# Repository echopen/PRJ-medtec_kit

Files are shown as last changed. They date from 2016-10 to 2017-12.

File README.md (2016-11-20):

# Project


## Name
[`PRJ-medtec_kit`]()

## Title @lang=fr
Projet de kit d'expérimentation

## Title @lang=en
Experiment kit project

## About @lang=en
Designing a modular hardware development kit to spread the project and raise contributions.

## Challenge
[`CHG-medtec`]()

## Uses
This repository provid all is needed to make an echOpen kit. It is divided in six folders:  
+ **configurations**, in this folder one find the different working configuration to have a functional kit. It lists the différent daughter board to plug on a mother and the mecanic modules used.  
+ **electronic**, in this folder one can find the daughter boards sources, plans... And to software for the microcontrolers or FPGA.  
+ **installation**, in this folder one can find the instruction to download and install the software need by your computer (linux or windows user). There is also the instructions for installing boards such as arduino or RedPitaya and how to launch the kit.  
+ **license**, in this folder one can find the echOpen license.  
+ **mecanic**, in this folder one can find the sources for mecanic pieces.  
+ **miscellanous** contain informations about functions and interfaces.

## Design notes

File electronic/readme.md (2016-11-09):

# Informations

This folder contains the informations and sources to build the electrical parts (daughter boards) of our kit. It is composed of the folders:  
- **daughter_boards**, daughter board informations  
- **miscellianous**, kicad librairy files and datasheets of the electronic parts  
- **modules**, modules informations  

# Uses

If you want to access the informations and the sources a given daughter board juste go in the daughter_board folder (./daughter_board/DVC-) you are interesting in. Open the readme file with a markdown display tool (such as retext) where their is the needed information, the source are accessible simply by clicking on the link.

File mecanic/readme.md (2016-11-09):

# Informations

This folder contains the informations and sources to build the mecanical device for our kit. It is composed of two folders: **device** and **modules**. 

# Uses

If you want to access the informations and the sources a given device juste go in the device folder (./device/DVC-) you are interesting in. Open the readme file with a markdown display tool (such as retext) where their is the needed information, the source are accessible simply by clicking on the link.

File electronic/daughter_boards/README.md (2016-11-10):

In this repository one can find the different daughter boards of our systeme. Each daughter board can have different version.

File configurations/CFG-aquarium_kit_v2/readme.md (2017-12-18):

# Configuration
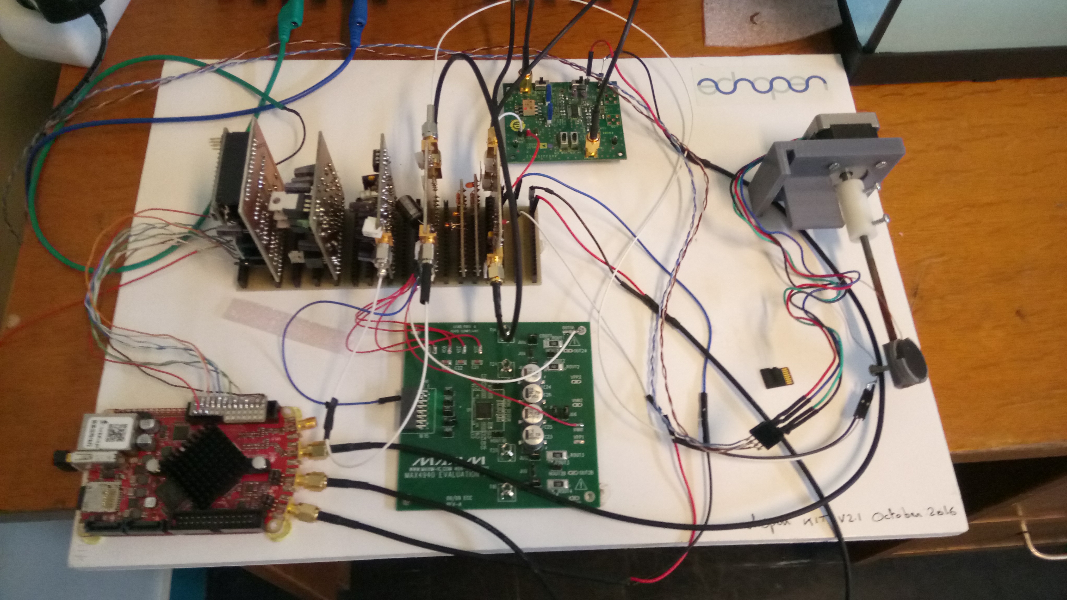
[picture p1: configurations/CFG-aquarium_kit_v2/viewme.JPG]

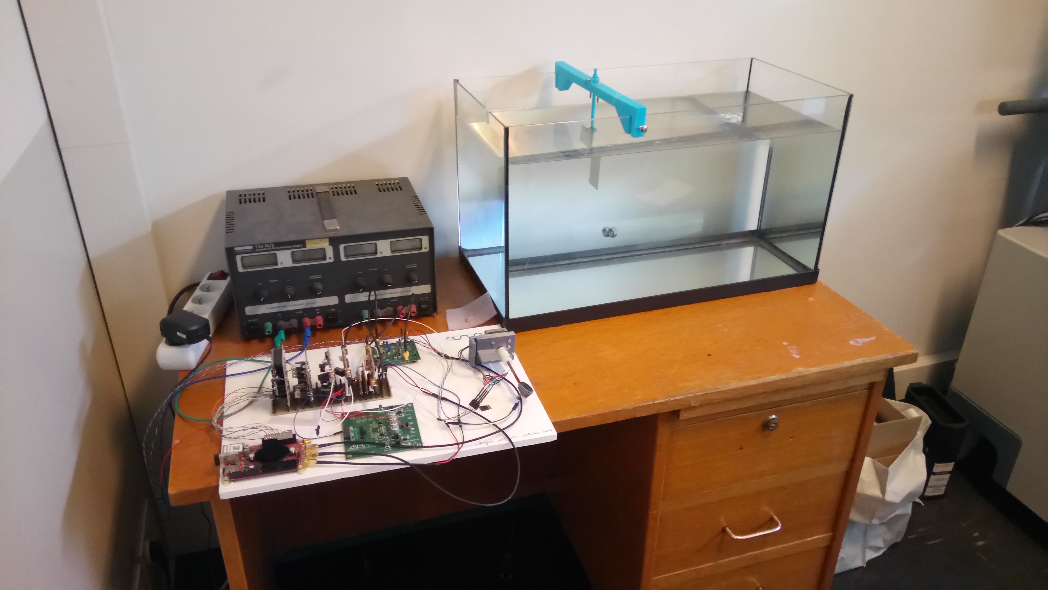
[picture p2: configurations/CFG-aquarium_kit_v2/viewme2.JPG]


## Name
[`CFG-aquarium_kit`]()

## Title
Kit 3.1 - Sept 2017

## About

## Uses
* [`DVC-aquarium`](../../mecanic/device/DVC-aquarium)
* [`MDL-transducer_v4`](../../electronic/modules/hardware/MDL-transducer/MDL-transducer_v4)
* [`MDL-power_supply_v1`](../../electronic/modules/hardware/MDL-power_supply/MDL-power_supply_v1)
* [`MDL-mother_board_v1`](../../electronic/modules/hardware/MDL-mother_board)
* [`MDL-redpitaya`](../../electronic/modules/hardware/MDL-redpitaya)
* [`MDL-motor_v2`](../../electronic/modules/hardware/MDL-motor/MDL-motor_v2)
* [`DB-supply_v1`](../../electronic/daughter_boards/DB-supply/DB-supply_v1)
* [`DB-high_voltage_v1`](../../electronic/daughter_boards/DB-high_voltage/DB-high_voltage_v1)
* [`DB-motor_control_v3`](../../electronic/daughter_boards/DB-motor_control/DB-motor_control_v3)
* [`DB-pulser_v3`](../../electronic/daughter_boards/DB-pulser/DB-pulser_v3)
* [`DB-filter_v1`](../../electronic/daughter_boards/DB-filter/DB-filter_v1)
* [`DB-envelope_detector_v1`](../../electronic/daughter_boards/DB-envelope_detector/DB-envelope_detector_v1)
* [`DB-tr_switch_tgc_v2`](../../electronic/daughter_boards/DB-tr_switch_tgc/DB-tr_switch_tgc_v2)

The sources of the code can be found [here](../../electronic/modules/software), select your configuration. Details on how to put the code on the arduino and the RedPitaya can be found [here](../../installation/linux_user/readme.md).

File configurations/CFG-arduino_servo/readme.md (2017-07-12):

# Configuration
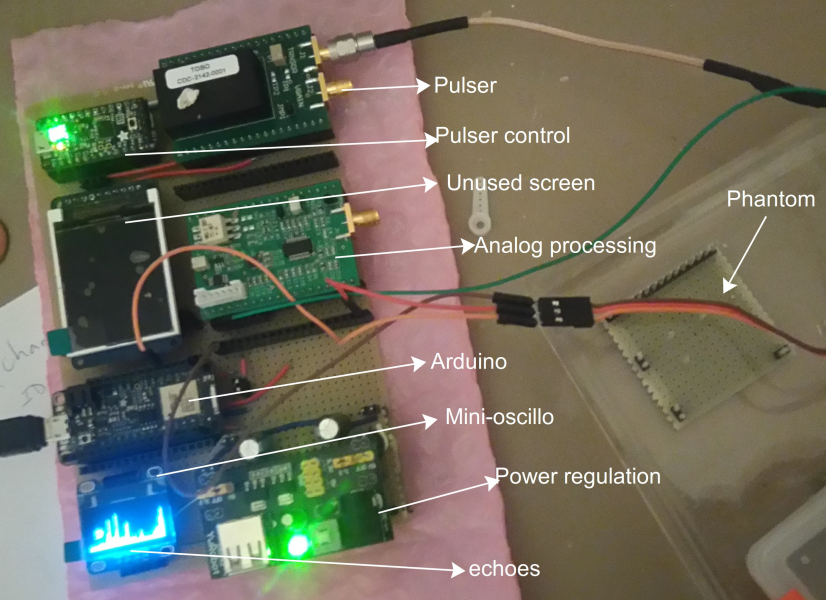
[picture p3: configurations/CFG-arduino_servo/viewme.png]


## Name
[`CFG-arduino_servo`]()

## Title
Dev kit v.1.1

## About

## Uses

* [`MDL-pulser_control`](../../electronic/modules/hardware/MDL-pulser_control)
* [`MDL-piezoservo`](../../electronic/modules/hardware/MDL-power_supply/MDL-piezoservo)
* [`MDL-breadboard_supply`](../../electronic/modules/hardware/MDL-breadboard_supply)
* [`MDL-analog_processing_ic`](../../electronic/modules/hardware/MDL-analog_processing_ic)
* [`MDL-pulser_ic`](../../electronic/modules/hardware/MDL-pulser_ic)
* [`MDL-arduino_wifi_daq`](../../electronic/modules/hardware/MDL-arduino_wifi_daq)

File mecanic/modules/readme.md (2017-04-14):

To make the kit, one will have to print (with a 3d printer):
- MDL-motor_support wich is the part where we will fix the motor, this part afer will be put on an aquarium border. Need to precise the screw to put on (x4)
- MDL-rod_fixation wich is a piece to link a metal rod (MDL-rod) with the motor. There is two holes to put 2 screw the upper one (motor size) need to stick out so it will hit the motor_support when initialising (searching it's 0). The second one use to fix the rod. (diameter of the screw)
MDL-transducer depend on your transducer better to make your own. When we will have (ENS) typical transducer we will make an appropritate support.

MDL-phantom_support depend on the size of you aquarium (this one is for xxx mm large).
MDL-stick must be place in MDL-phantom
MDL-plate_support was made to put a thin plate for tests. It plug with MDL-stick
The three last MDL are not necessary

For 3dprinting use MDL-x.stl files. If you want to make modifications one can use freecad (open the .igs file) modify and then export in .stl file (mesh formats files).

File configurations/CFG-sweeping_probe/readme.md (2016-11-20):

# Configuration
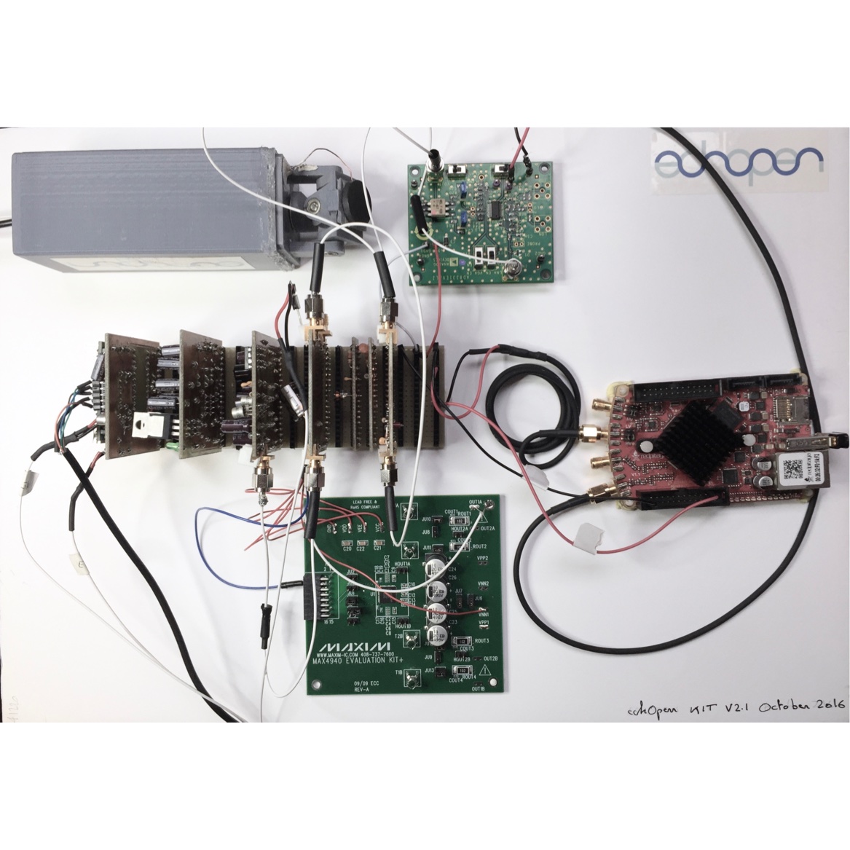
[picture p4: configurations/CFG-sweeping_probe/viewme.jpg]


## Name
[`CFG-sweeping_probe`]()

## Title
Kit 2.1 - Oct 2016

## About

## Uses
* [`DVC-sweeping_probe`](../../mecanic/device/DVC-sweeping_probe)
* [`MDL-transducer_v4`](../../electronic/modules/hardware/MDL-transducer/MDL-transducer_v4)
* [`MDL-power_supply_v1`](../../electronic/modules/hardware/MDL-power_supply/MDL-power_supply_v1)
* [`MDL-mother_board_v1`](../../electronic/modules/hardware/MDL-mother_board)
* [`MDL-redpitaya`](../../electronic/modules/hardware/MDL-redpitaya)
* [`DB-supply_v1`](../../electronic/daughter_boards/DB-supply/DB-supply_v1)
* [`DB-high_voltage_v1`](../../electronic/daughter_boards/DB-high_voltage/DB-high_voltage_v1)
* [`DB-motor_control_v1`](../../electronic/daughter_boards/DB-motor_control/DB-motor_control_v1)
* [`DB-pulser_v2`](../../electronic/daughter_boards/DB-pulser/DB-pulser_v2)
* [`DB-filter_v1`](../../electronic/daughter_boards/DB-filter/DB-filter_v1)
* [`DB-envelope_detector_v1`](../../electronic/daughter_boards/DB-envelope_detector/DB-envelope_detector_v1)
* [`DB-tr_switch_tgc_v1`](../../electronic/daughter_boards/DB-tr_switch_tgc/DB-tr_switch_tgc_v1)

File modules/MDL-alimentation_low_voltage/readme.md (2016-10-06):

# Module
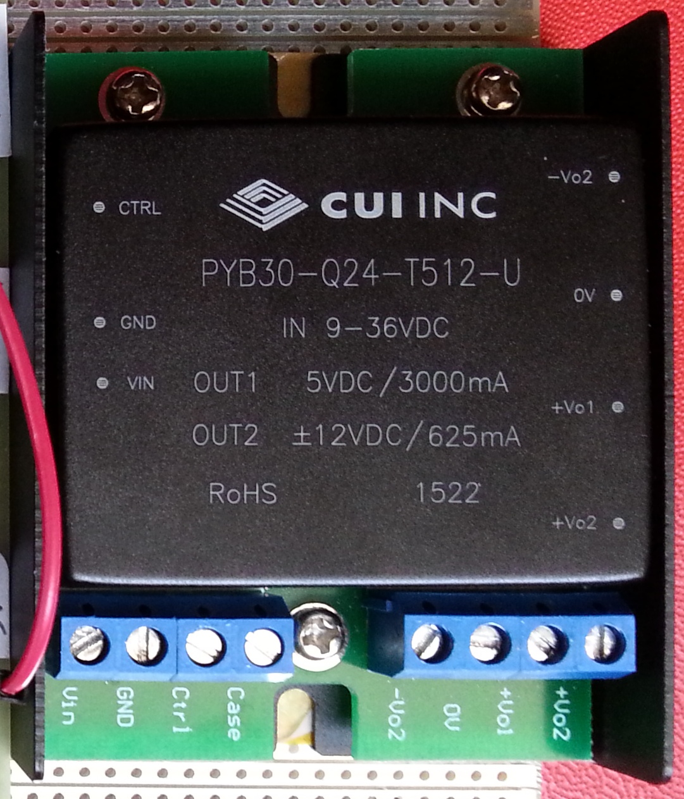
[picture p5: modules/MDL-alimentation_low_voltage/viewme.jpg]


## Name
[`MDL-alimentation_low_voltage`]()

## Title
Low voltage (+5v, +3.3v, ...) alimentation

## Description

## Uses
* external +5v

## Produce
* [`ITF-10_gnd`](../../interfaces/ITF-10_gnd)
* [`ITF-29_5v`](../../interfaces/ITF-29_5v)

## Functions
* TODO, ex : [`FCT-sensing`](../../functions/FCT-sensing)

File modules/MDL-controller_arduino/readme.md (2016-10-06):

# Module
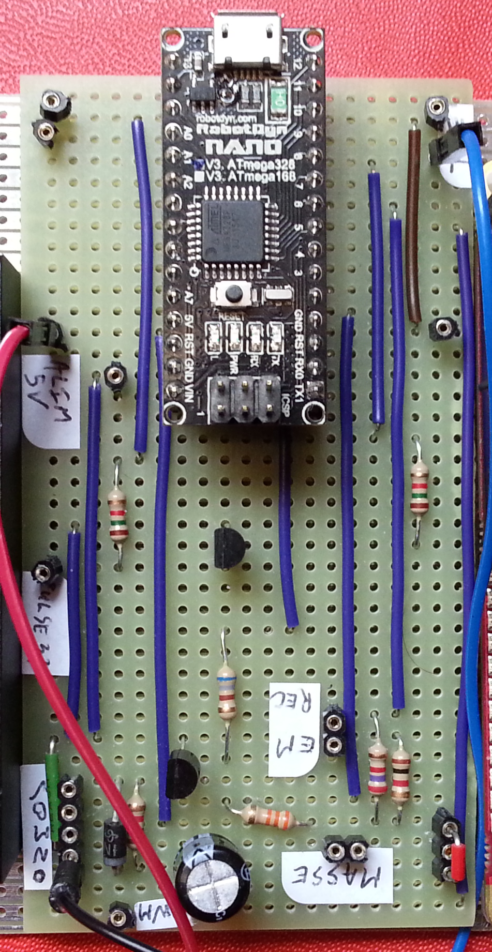
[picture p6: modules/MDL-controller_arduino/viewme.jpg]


## Name
[`MDL-controller_arduino`]()

## Title
Arduino µC with E/S for driving CC motor

## Description

## Uses
[`ITF-10_gnd`](../../interfaces/ITF-10_gnd)

## Functions
TODO, ex : [`FCT-sensing`](../../functions/FCT-sensing)

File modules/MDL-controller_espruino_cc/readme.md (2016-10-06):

# Module
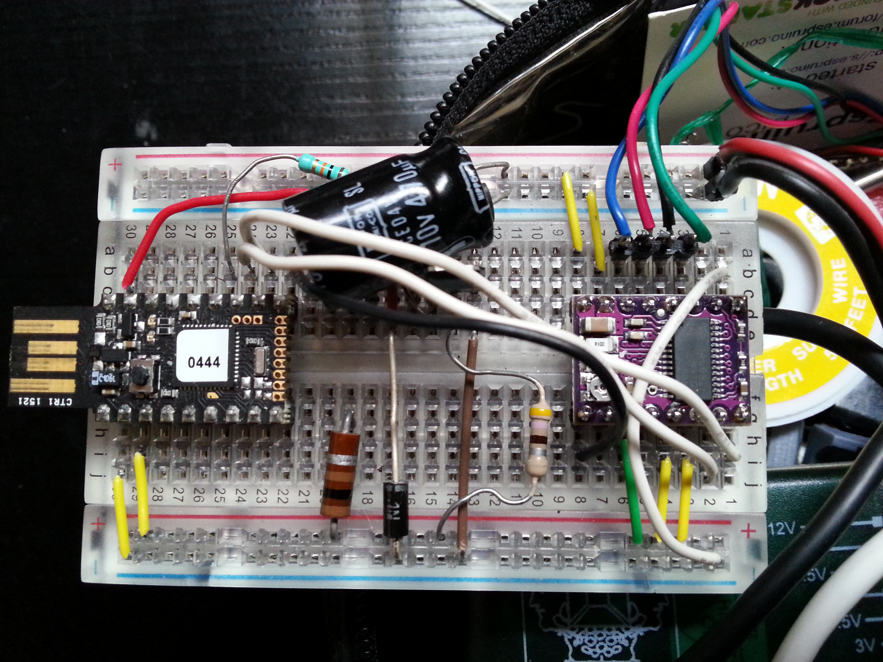
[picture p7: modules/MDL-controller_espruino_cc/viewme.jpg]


## Name
[`MDL-controller_espruino_cc`]()

## Title
Espruino µC with E/S for driving CC motor

## Description

## Uses
[`ITF-10_gnd`](../../interfaces/ITF-10_gnd)

## Functions
TODO, ex : [`FCT-sensing`](../../functions/FCT-sensing)

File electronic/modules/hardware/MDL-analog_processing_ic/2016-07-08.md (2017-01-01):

# First hands-on with Goblin : an overview [](@description First experiment on 08th July 2016)

## What does it do?

This [Goblin](/electronic/modules/hardware/MDL-analog_processing_ic/) board aims at getting a signal, and giving access to key points within the signal processing chain for ultrasound imaging, namely:

* Getting access to a TGC
* Getting the enveloppe of the signal
* Cleaning the signal before feeding in the on-board SPI ADC

All key signals are accessible, and jumpers, as well as pots, enable on-board fine-tuning of the signals. [See more details on the __testing session__, to see the behavior of the board on a oscillo](/electronic/modules/hardware/MDL-analog_processing_ic/2016-07-08.md).

## View

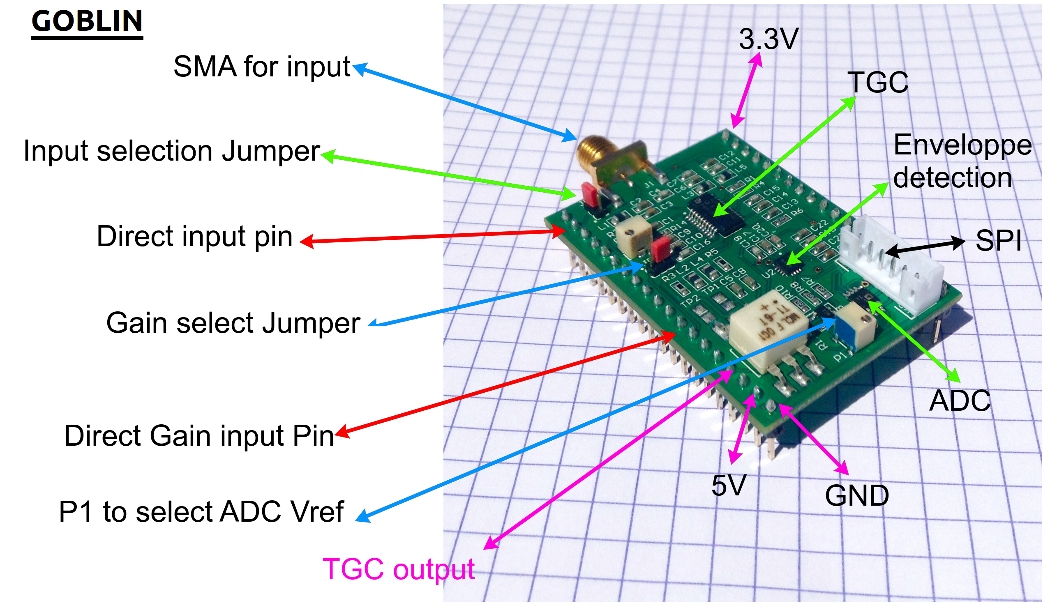
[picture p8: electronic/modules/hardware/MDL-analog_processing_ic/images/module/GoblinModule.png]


## Detailed view

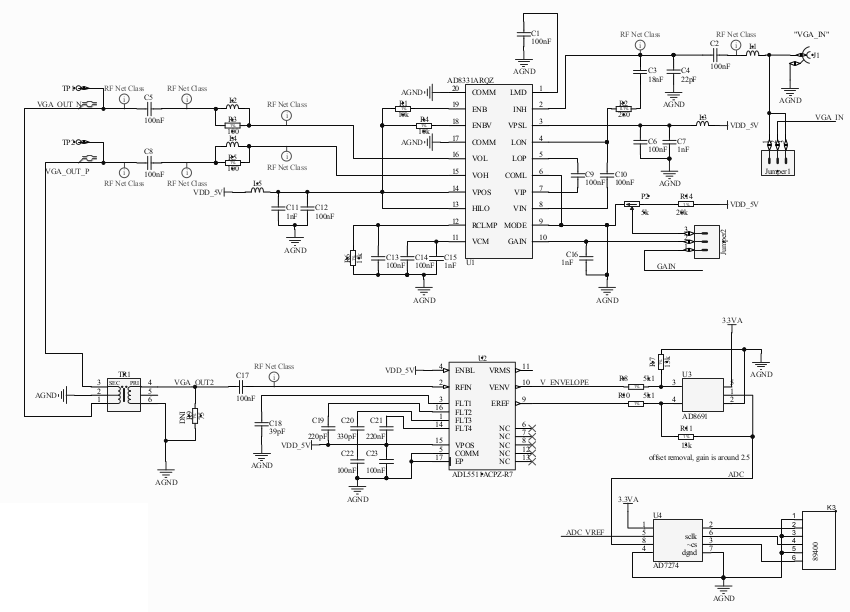
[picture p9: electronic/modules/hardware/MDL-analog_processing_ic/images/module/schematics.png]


## Principles

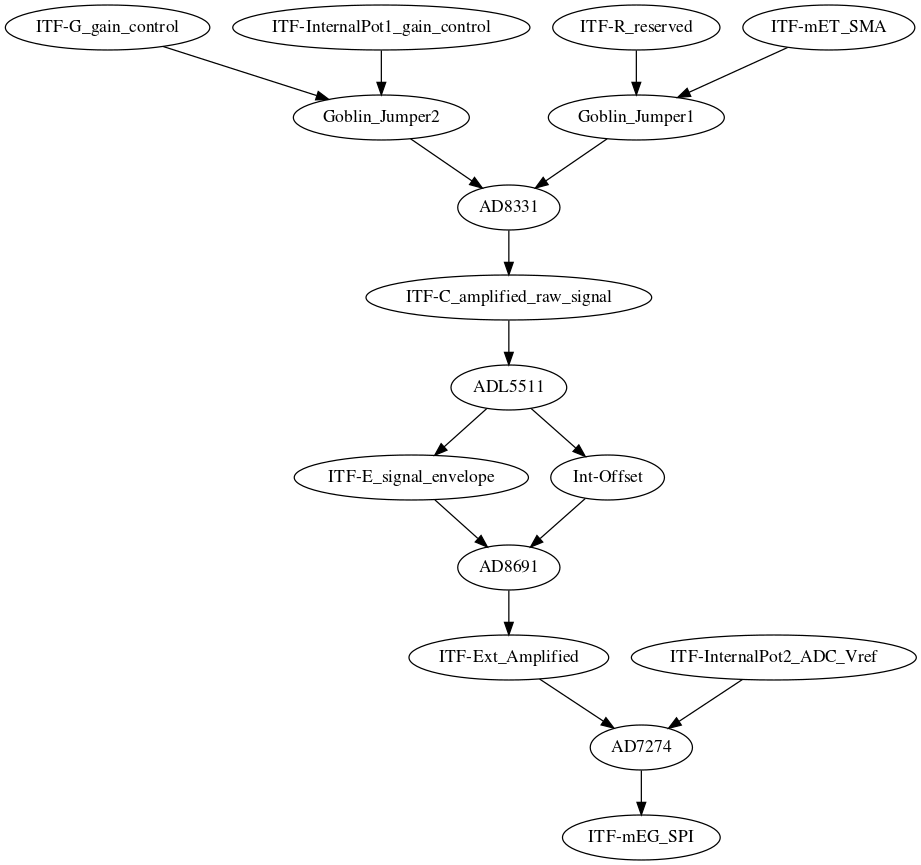
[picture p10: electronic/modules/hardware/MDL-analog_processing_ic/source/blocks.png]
Block schema


## Testing the board

### Signal in vs Signal out of the TGC

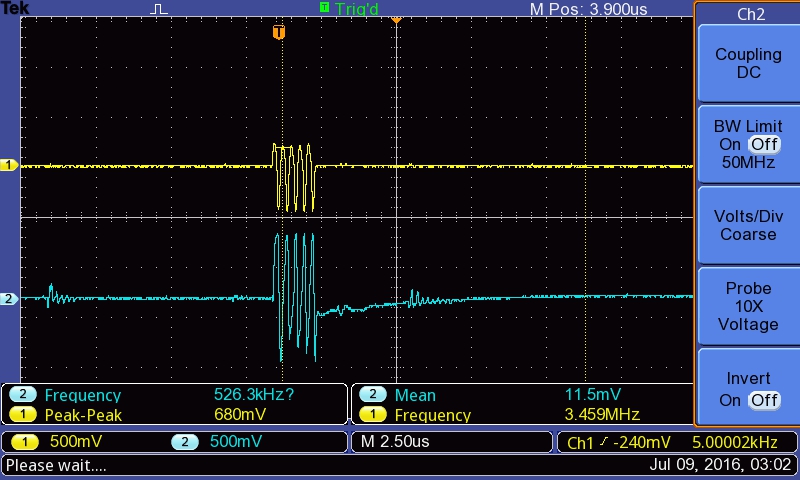
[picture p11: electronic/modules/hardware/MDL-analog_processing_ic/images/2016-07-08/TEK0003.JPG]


### Trying with different frequencies

#### At 3 MHz

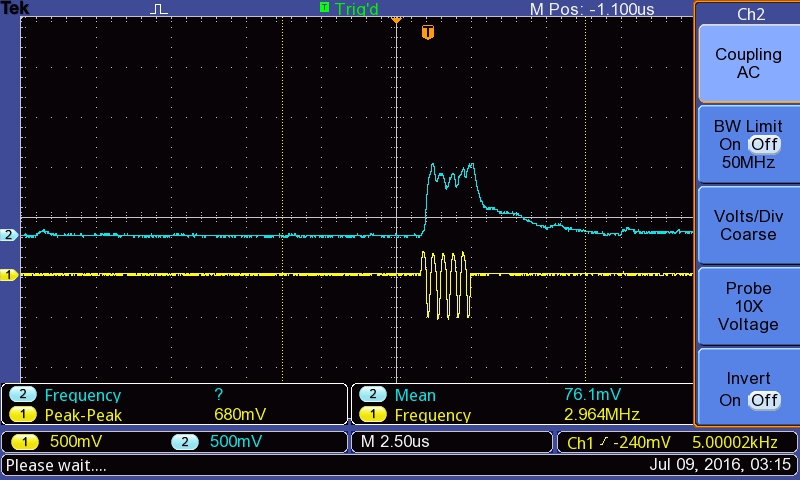
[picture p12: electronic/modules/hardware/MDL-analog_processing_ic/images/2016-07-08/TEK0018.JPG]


#### At 5MHz

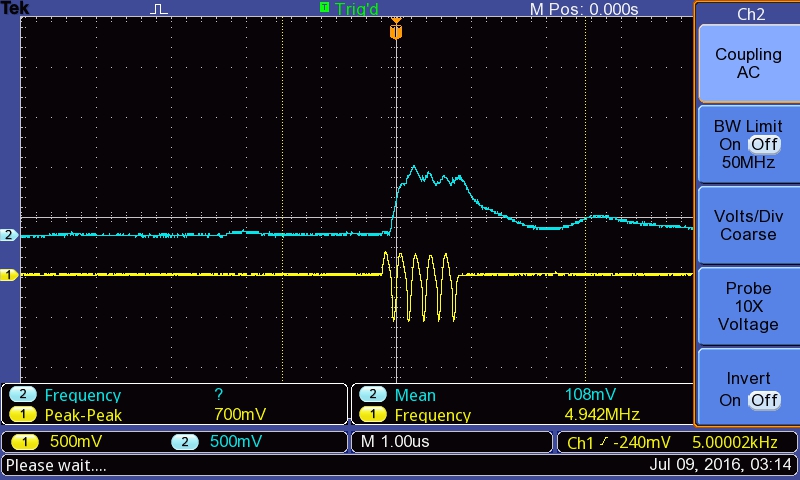
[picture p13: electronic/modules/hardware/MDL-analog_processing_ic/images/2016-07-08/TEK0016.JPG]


#### At 7.5MHz

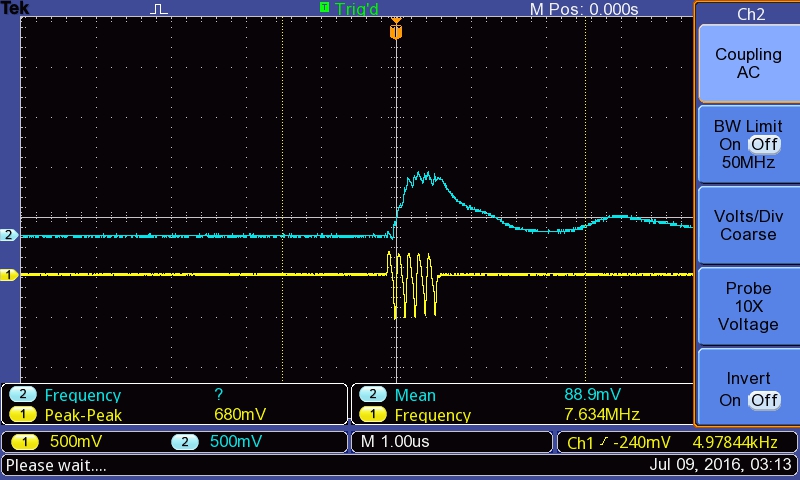
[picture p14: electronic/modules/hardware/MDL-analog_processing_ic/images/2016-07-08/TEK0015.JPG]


#### At 10MHz

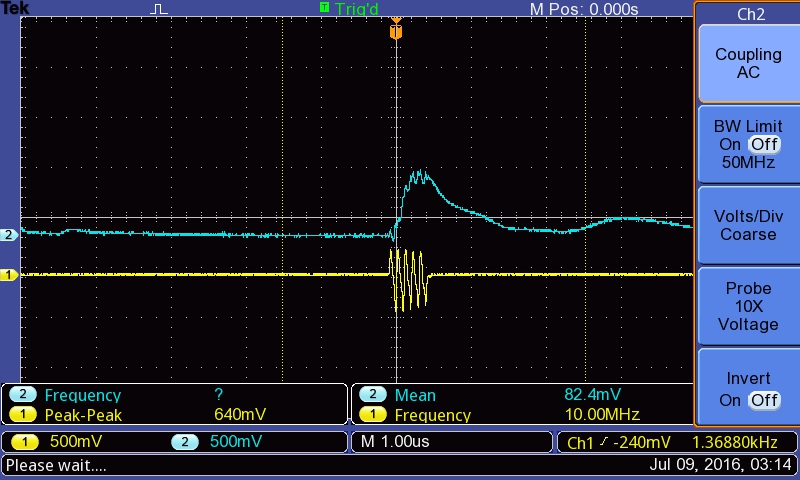
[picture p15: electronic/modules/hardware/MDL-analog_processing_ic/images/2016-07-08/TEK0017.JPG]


### Difference between enveloppe and ADC input?

-> the offset is removed, there's also a small gain (x2).

See below: there's an offset at the enveloppe detection (~RMS), which is removed. Enveloppe is 500mV before, comes at 1V+ afterwards.

#### Before the AOP

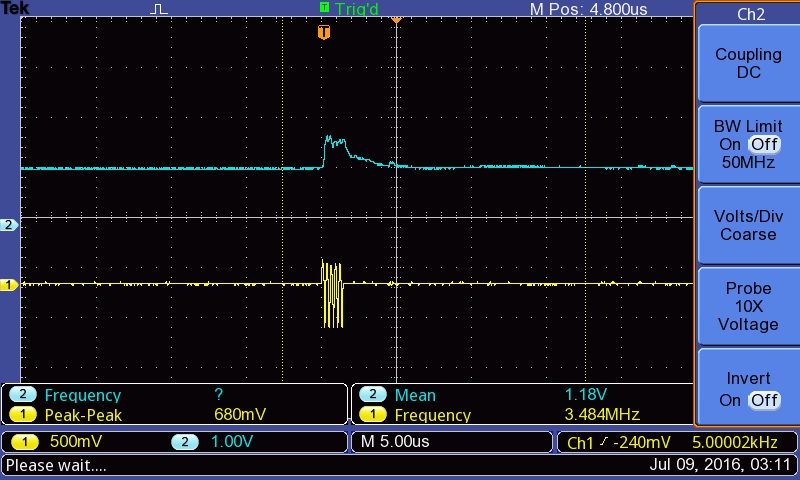
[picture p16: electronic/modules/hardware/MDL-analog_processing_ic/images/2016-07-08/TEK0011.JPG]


#### After the AOP

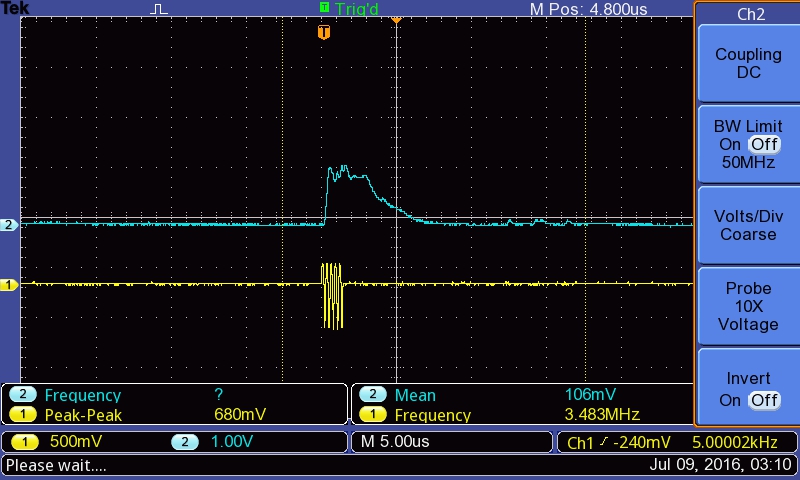
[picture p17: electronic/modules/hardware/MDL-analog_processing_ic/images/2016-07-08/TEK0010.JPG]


TODO: Table

## To know more

### Components that have been used

* TGC:
* Enveloppe detection:
* ADC:

TODO =)

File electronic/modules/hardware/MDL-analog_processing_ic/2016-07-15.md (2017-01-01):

# Second hands-on with Goblin : an overview [](@description Second work with Goblin)

## What does it do?

This [Goblin](/electronic/modules/hardware/MDL-analog_processing_ic/) board aims at getting a signal, and giving access to key points within the signal processing chain for ultrasound imaging, namely:

* Getting access to a TGC
* Getting the enveloppe of the signal
* Cleaning the signal before feeding in the on-board SPI ADC

All key signals are accessible, and jumpers, as well as pots, enable on-board fine-tuning of the signals. [See more details on the __testing session__, to see the behavior of the board on a oscillo](/electronic/modules/hardware/MDL-analog_processing_ic/2016-07-08.md). __Beware, this session had a poor energy supply quality, so the 5V got quite low. The [new log](/electronic/modules/hardware/MDL-analog_processing_ic/2016-07-15.md), covers it better.

## Testing the board using 0.2V in gain input (max can be 1V, that's ~20% gain used)

### Just after the TGC : A 60mV signal becomes a 300mV signal.

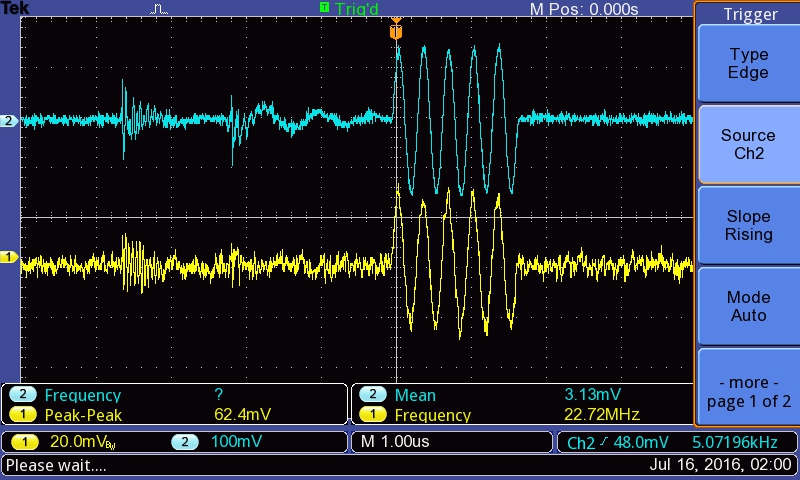
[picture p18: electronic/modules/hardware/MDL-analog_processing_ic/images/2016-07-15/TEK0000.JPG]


### Which becomes, after enveloppe detection, a 400mV enveloppe.

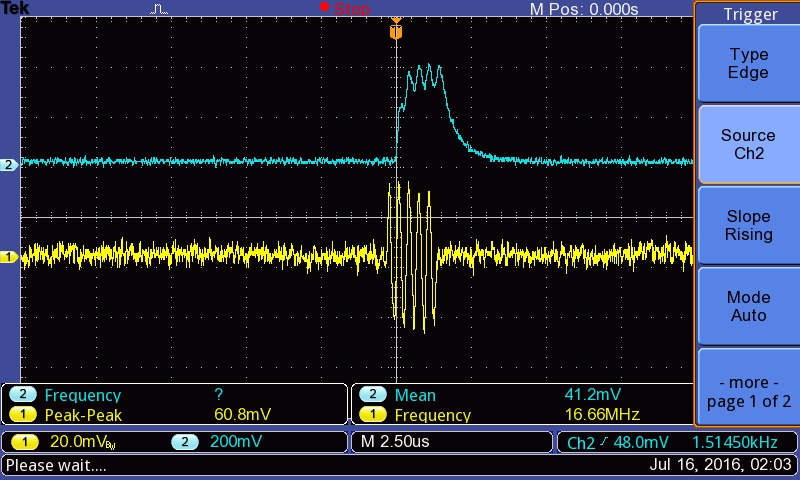
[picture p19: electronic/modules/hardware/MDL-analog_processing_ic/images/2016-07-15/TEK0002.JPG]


### Likewise, a 120mVpp signal becomes a 750mV enveloppe, clean.



## View



## Detailed view



## Principles

Block schema

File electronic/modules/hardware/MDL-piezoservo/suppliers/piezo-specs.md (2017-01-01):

# Interested in a monoelement transducer for an open science project

Dear XXX,

I'm currently working with an open-source echography association  (echopen.org) based in Paris, which is currently looking for transducers that could be used for medical imaging for the design of its tool. I have heard your name through former colleagues at the ESPCI Paristech, and would like to investigate if you could provide us with appropriate transducers for this project.
 
We are developing a mechanical, single-element-design probe, operating at three frequencies, so with three series of piezos, with the following details:

* One at 3.5 MHz, focal zone between 50 and 150 mm,
* One at 5 MHz , focal zone between 30 and 105 mm,
* One at 7.5 MHz , focal zone between 10 and 75 mm.

With respect to the dimensions, ideally, we are looking for a low-footprint transducer (less than 2 cm diameter) and minimal depth for the physical size of the transducer (we don't need casing, though we'd need the backing and soldering already done) to integrate in our prototype. We'll be finetuning additional parameters as soon as we make progress on the probe itself. we would need:

* Diameter: as small as possible, ideally below 15mm for the 3.5MHz, 8mm for the 5MHz and 5mm for the 7.5MHz - without casing.
* Thickness: as small as possible.

Would it be possible for you to provide us with a quote for a first, to test one, along with the corresponding specs? Also, even using rough figures, we'd be keen on having an idea of the budget that'd be required to produce a couple, from 2 or 3 to 50 at the prototyping stage.

Looking forward to reading from you,

Best regards,

Luc

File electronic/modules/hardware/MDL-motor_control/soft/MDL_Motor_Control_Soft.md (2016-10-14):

Module: MDL_Motor_Control_Hard

Function: sensing

Sub-Function: emitting

We use a single transducer, it must sweep an given angle in order to make 2D imaging, this can be done with a movement convertor. But if we want to uniformely scan the angle, we have to know exactly where and when the transducer is located. Depend on the solution, this can be ordered or calculated by the software.

Solutions: 

version: V1.0

date: 15/04/2016

technology: home made

contributor: Jérôme

Source:

[https://github.com/echopen/Prototype_software/blob/master/V1/Arduino/motor_pulse/motor_pulse.ino](https://github.com/echopen/Prototype_software/blob/master/V1/Arduino/motor_pulse/motor_pulse.ino)

An API will be made soon.

Flowchart:

The function Velocity is made on interruption, each time the encoder of the motor change from LOW to HIGH level, the velocity is calculated. Due to RedPitaya speed limitation (on measurement), with have limited the motor "virtual" velocity to Vlim. So even if the motor is too fast, the time between two pulse will be long enough to make an acquisition.

The function Interpolation determine the angle difference of the motor position between each pulse. With this angle and the instantaneous velocity we can determined the time between each pulse. The interpolation function give a constant dz on a line perpendicular to the probe.

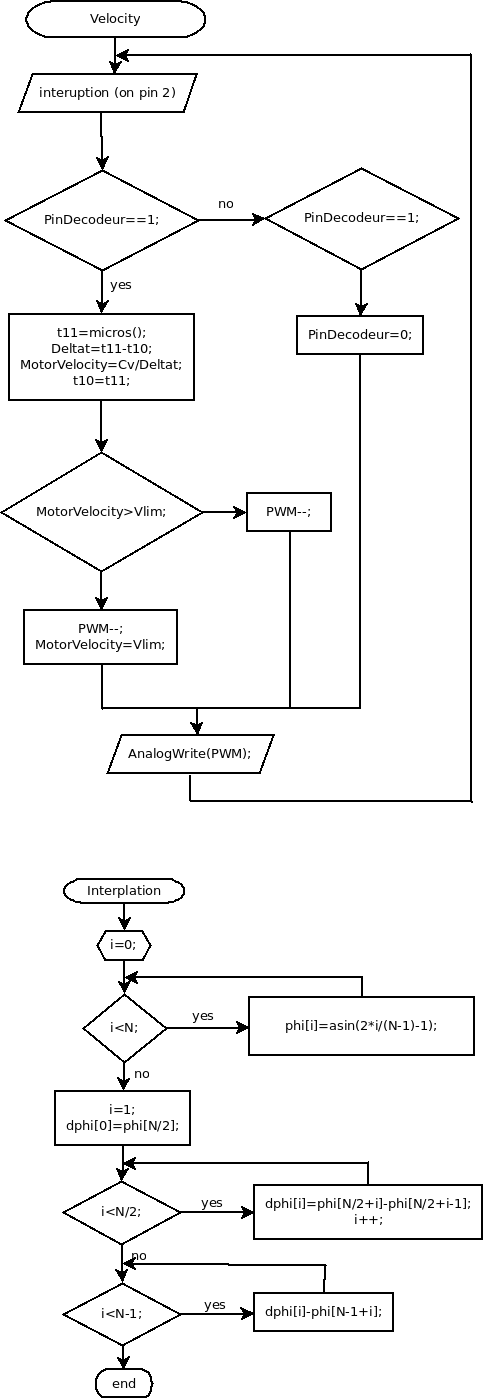
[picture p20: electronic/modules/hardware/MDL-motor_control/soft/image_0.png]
image alt text


version: V2.0

date: 07//2016

technology: IC

contributor: Feng

Source:

[https://github.com/echopen/Prototype_software/blob/master/Arduino_Nano/Stepper_Motor/stepper%20motor.ino](https://github.com/echopen/Prototype_software/blob/master/Arduino_Nano/Stepper_Motor/stepper%20motor.ino)

An API will be made soon.

Flowchart:

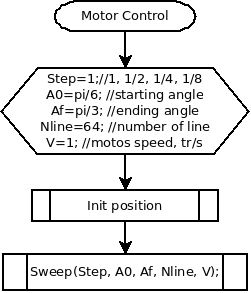
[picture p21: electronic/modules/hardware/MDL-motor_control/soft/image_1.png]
image alt text


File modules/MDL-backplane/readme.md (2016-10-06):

# Module
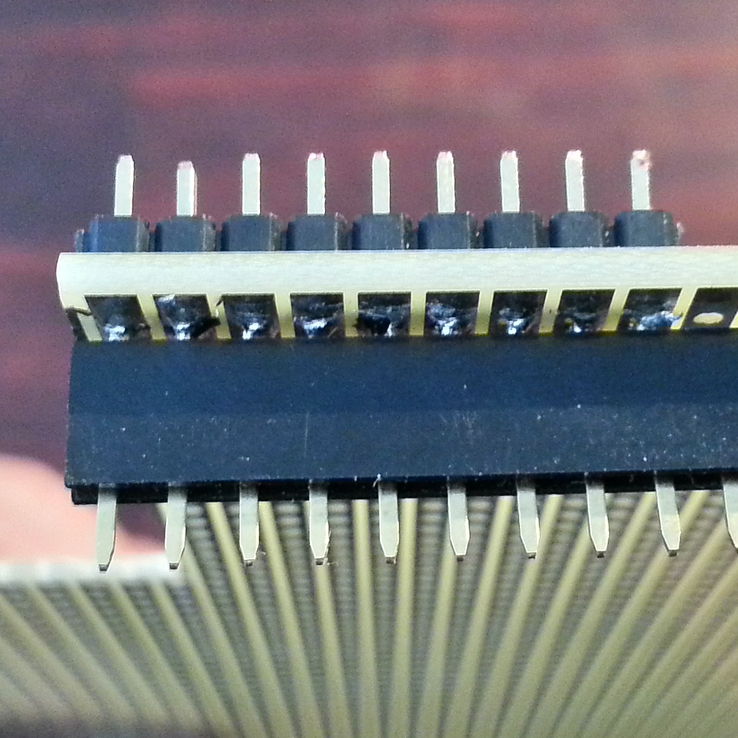
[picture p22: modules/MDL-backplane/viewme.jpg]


## Name
[`MDL-backplane`]()

## Title
Backplane card

## Description

## Uses
[`ITF-10_gnd`](../../interfaces/ITF-10_gnd)

## Functions
TODO, ex : [`FCT-sensing`](../../functions/FCT-sensing)

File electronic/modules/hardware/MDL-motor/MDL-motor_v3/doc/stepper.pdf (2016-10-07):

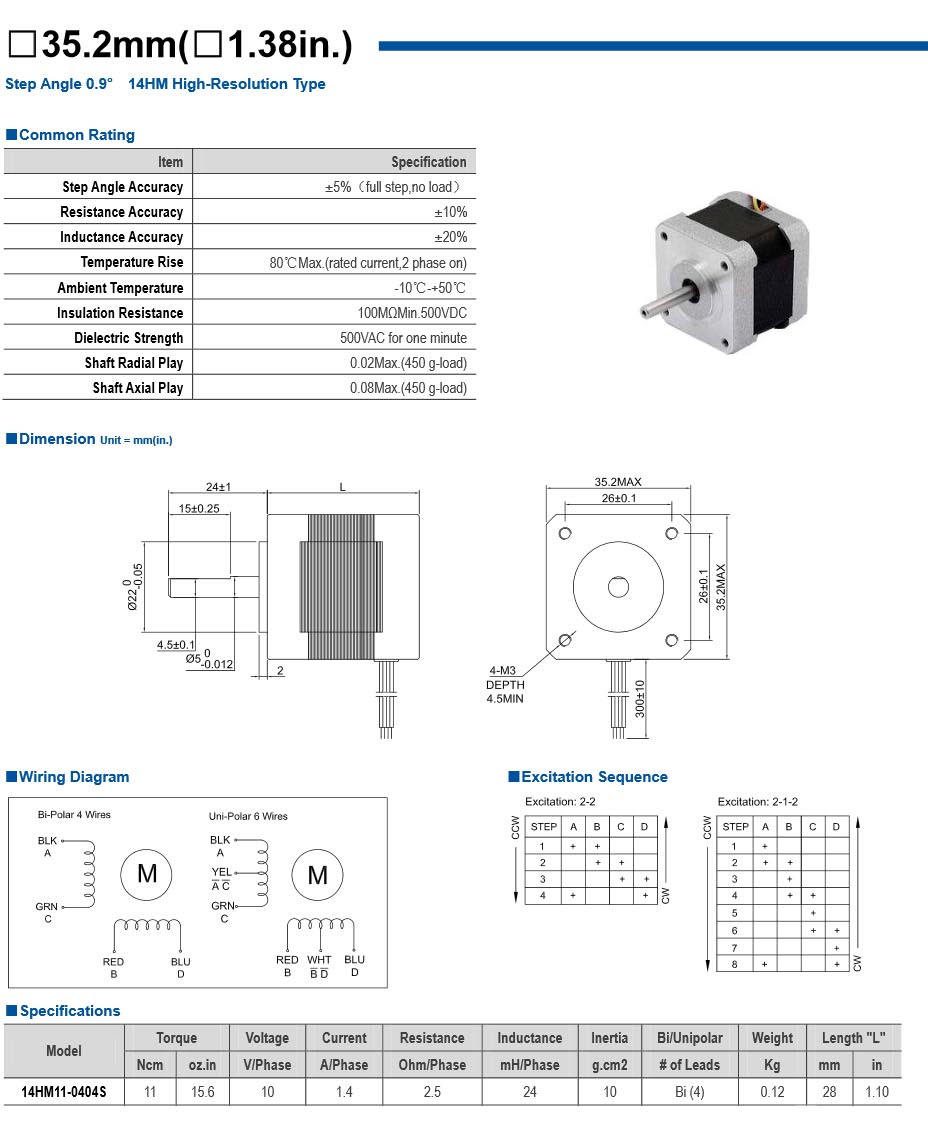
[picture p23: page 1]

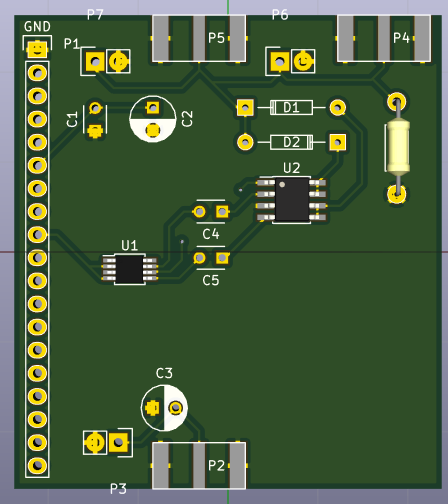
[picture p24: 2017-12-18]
electronic/daughter_boards/DB-pulser/DB-pulser_v3/images/pcb.png

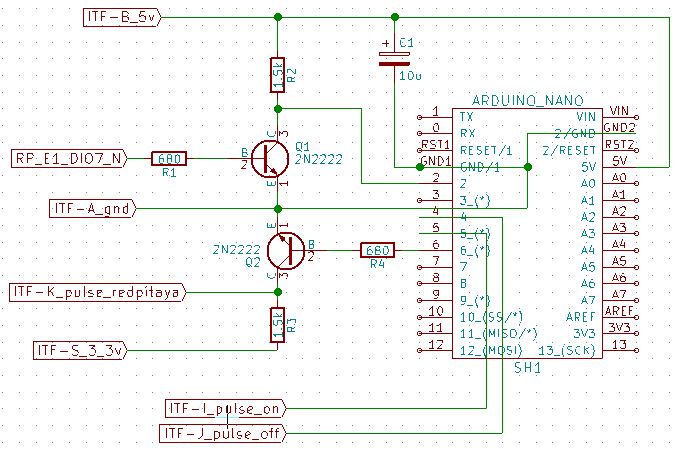
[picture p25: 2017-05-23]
electronic/modules/hardware/MDL-ucontroler/MDL-ucontroler_v2/images/scheme.png

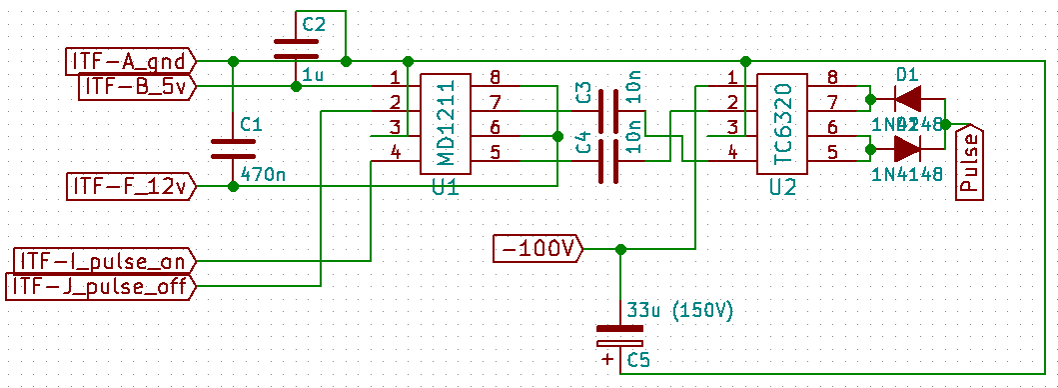
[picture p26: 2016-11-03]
electronic/modules/hardware/MDL-pulser/MDL-pulser_v3/images/scheme.png

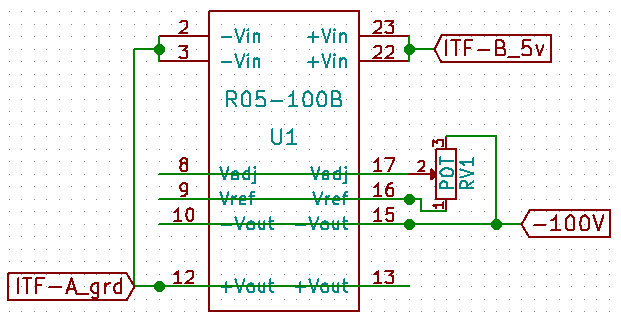
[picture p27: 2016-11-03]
electronic/modules/hardware/MDL-high_voltage/MDL-high_voltage_v2/images/scheme.png

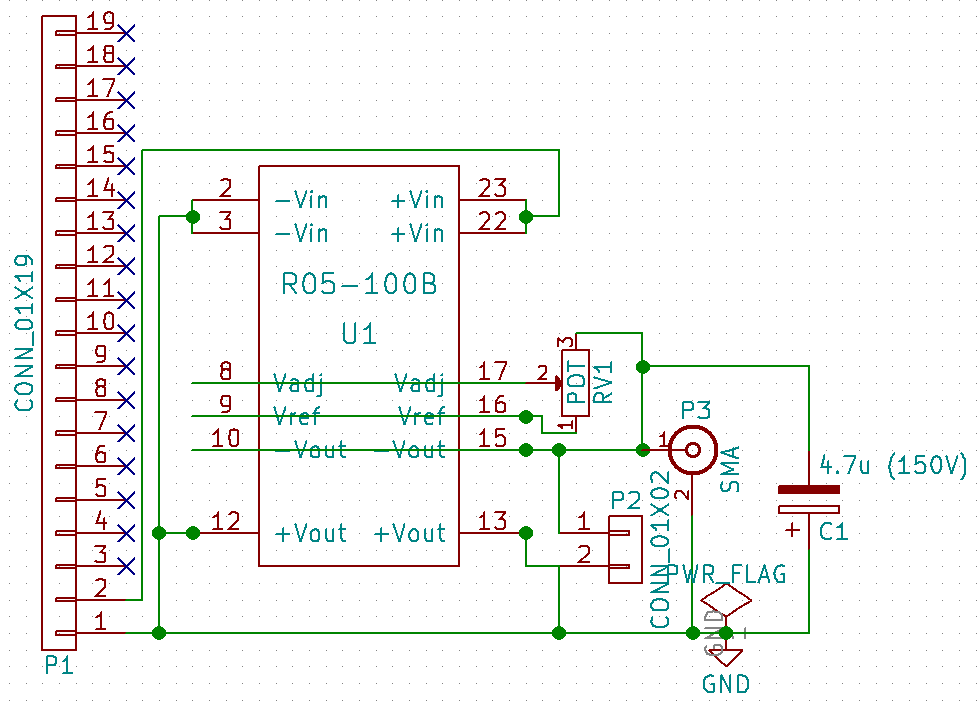
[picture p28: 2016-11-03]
electronic/daughter_boards/DB-high_voltage/DB-high_voltage_v2/images/scheme.png

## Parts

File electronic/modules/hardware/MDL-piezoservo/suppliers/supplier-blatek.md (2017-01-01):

### Info  [](@description supplier source file)

* Name: Blatek
* Site: http://blatek.com
* Contact: sales@blatek.com, Dr. Geng <geng@blatek.com> (VP/CTO), Randy Cyron <randyc@blatek.com>, Kevin Knarr <kevink@blatek.com>

### Status

* Deja contactes en 2015 
* Retour 2/1/16: be back with quotes
* Feedback OK - waiting input from team

### Notes

#### 2015

* Contact with Dr. Geng
* We do have a 3.5 MHz transducer. This transducer has a very low profile (4mm) and the active diameter is 17 mm. the focal length is 125 mm. The overall diameter is 19.5 mm. 
* Price 350$ / pc, 100USD as bottom line for bigger volumes.

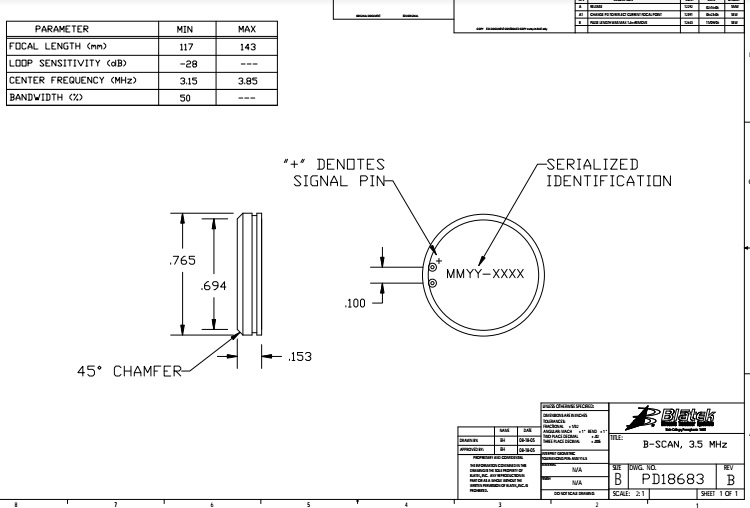
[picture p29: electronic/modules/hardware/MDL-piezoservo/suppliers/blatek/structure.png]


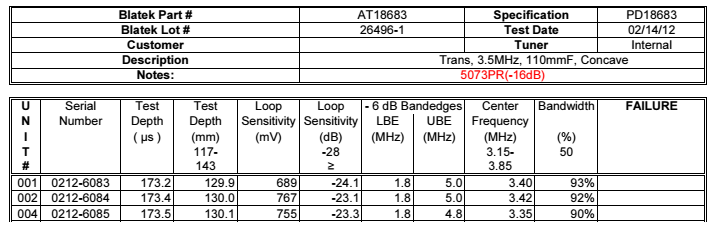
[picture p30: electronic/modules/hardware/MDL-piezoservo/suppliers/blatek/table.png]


* __Rmq:__  Based on your focal zone requirement you need the transducers with a F# about 6 to achieve the results you need. I used a formulae as below,-3dB focal zone =7.1 x wavelength x F#^2, here F#=focal length/aperture

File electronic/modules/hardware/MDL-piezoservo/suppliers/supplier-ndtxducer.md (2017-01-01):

### Info [](@description supplier source file)

* Name: NDTXducer
* Site: http://www.ndtxducer.com/
* Contact: Valdemar NDTXducer <valdemar@ndtxducer.com>

### Status

* Feedback OK (4/11/16) - waiting input from team

### Notes
 
* Recommanded by Okos ( amlynchyk@okos.com )

#### 1st Proposal

Attached is drawing for one of the transducers we make with UHF connector.
Will those outside dimensions work for you? We can change connector to BNC or Microdot or just provide it without any connector just wires.
In it we could make:

* 3.5MHz, 0.5” diameter with 3” Spherical Focus,     $277.0each
* 5.0MHz, 0.5” diameter with 3” Spherical Focus,     $277.0each
* 7.5MHz, 0.5” diameter with 3” Spherical Focus,     $320.0each

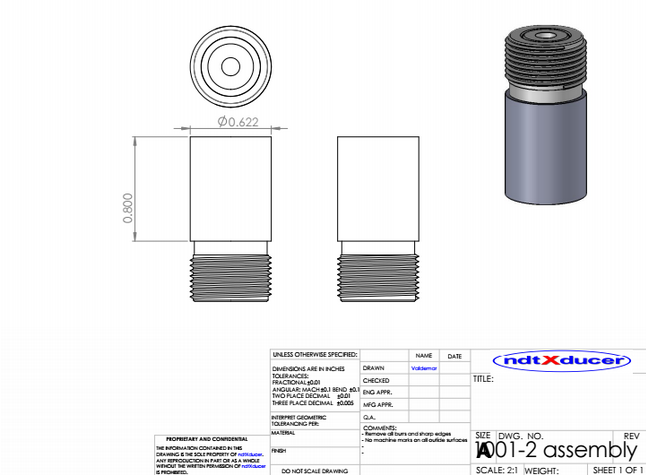
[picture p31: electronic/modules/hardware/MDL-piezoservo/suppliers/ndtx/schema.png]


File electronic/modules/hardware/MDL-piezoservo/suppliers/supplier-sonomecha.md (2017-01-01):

### Info [](@description supplier source file)

* Name: SonoMecha
* Site: http://www.sonomecha.com/
* Contact: sales@sonomecha.com

### Status

* Contact in 2015 (NA). 
* 275$/deux with off-the-shelf components
* Feedback OK - waiting input from team

### Notes
 
#### Echange in 2015

1. Which type do you want either higher amplitude oriented design transducer or wider bandwidth designed transducer?
2. Regarding Q1, if you can try to test both, it will better for more option.
3. Regarding transducer types, they are focused UT and unfocused UT. For the focused UT, the design of lens would not allowed to the lower costs. It means that the radius of curvature is 286mm,so the lens diameter is also so huge that the special design is required to match the tool. 
The actual diameter of element is 17mm,best but too much cost to make it.
4. Regarding unfocused UT, they are round type and rectangular type of piezo element. For round type, the actual diameter of piezo is 14.5mm and for rectangular type is 10x20mm based on our estimation of design. Both are matched to the focal point at 125mm.
5. For round type, we are doing experiment to match the diameter today. Due to the dia. around 15mm, the element
should be make the criteria by the mold size and sintering process of ceramics.  
6. For rectangular type, it is O.K. to meet your criteria.
7. The delivery would be max. 3 weeks, but will meet your two weeks.
8. The pricing is $300 for one UT, but 2 UTs are $500. In addition, the wire transfer fee is $25 and shipping fee(?).
    We need your shipping address to make a quote. (The shipping fee will calculates only if we know your address)

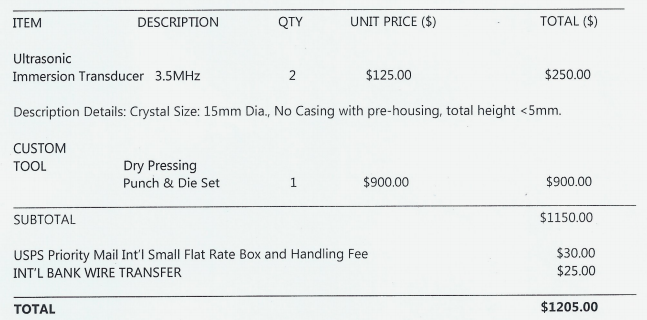
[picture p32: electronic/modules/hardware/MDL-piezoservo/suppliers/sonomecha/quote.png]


#### Feedback in 2016 for 3 different piezos

* With the said specs:
    * 3.5MHz. $400/ea
    * 5MHz $400/ea
    * 7.5MHz $450/ea
* Required 2pcs each
* Diameter as your specs.
* Bandwidth:70-80%
* Delivery:6-8wks

#### 10/11/16

* Also regarding 3.5MHz transducer, we can offer $250 per unit as sample 2-3 min.quantity. 
* For 50 units, we can offer $150.

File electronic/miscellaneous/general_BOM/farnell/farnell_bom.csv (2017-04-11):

Type | Reference | Quantity | Unitariy price | Total price
laboratory power supply | 2251946 | 1 | 68.24 | 68.24

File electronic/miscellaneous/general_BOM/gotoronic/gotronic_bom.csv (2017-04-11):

Type | Reference | Quantity | Unitariy price | Total price
stepper driver | 32726 | 1 | 6.6 | 6.6
stepper | 31115 | 1 | 17.8 | 17.8

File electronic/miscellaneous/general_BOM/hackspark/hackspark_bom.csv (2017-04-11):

Type | Reference | Quantity | Unitariy price | Total price
Socket 1*40 | https://hackspark.fr/fr/pack-of-80pcs-0-1-2-54mm-female-header-1-row-40-pins.html | 1 | 11.2 | 11.2
wires | https://hackspark.fr/fr/splittable-jumper-wires-200mm-40-pins.html | 1 | 5 | 5
soldering machin | https://hackspark.fr/fr/sp-80d-esd-soldering-station-sigital-eu-plug-80w-220-240v-1549.html | 1 | 84 | 84 | variable temperature
soldering machin | https://hackspark.fr/fr/sr-963-soldering-iron-eu-plug-40w-220-240v.html | 1 | 10 | 10 | cheap one
sn | https://hackspark.fr/fr/100g-no-pb-solder-with-silver-sn99ag0-3cu0-7-wire-0-7mm-100g-flux-f-sw26-no-clean.html | 1 | 10 | 10
unsolder tape | https://hackspark.fr/fr/chem-wikr-rosin-size-100-10-10l-10ft-3m.html | 1 | 3 | 3

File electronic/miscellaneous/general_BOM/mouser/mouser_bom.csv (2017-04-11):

SHOPPING BASKET
This is not an invoice
mars 21 | 2017 05:38:53
 | Mouser No | Mfr. No | Manufacturer | Customer No | Description | RoHS | Lifecycle | Order Qty. | Price (EUR) | Ext.: (EUR)
1 | 700-MAX4940EVKIT+ | MAX4940EVKIT+ | Maxim Integrated |  | Power Management IC Development Tools MAX4940 EVAL KIT | RoHS Compliant |  | 1 | 49 | 4 | 49 | 4
2 | 584-AD8331-EVALZ | AD8331-EVALZ | Analog Devices Inc. |  | Amplifier IC Development Tools AD8331 Eval Board | RoHS Compliant |  | 1 | 86 | 84 | 86 | 84
3 | 538-22-15-2026 | 22-15-2026 | Molex |  | Headers & Wire Housings 2.54MM BOARD CONN RA 2 CKT Tin | RoHS Compliant |  | 7 | 0 | 157 | 1 | 99
4 | 530-142-0701-801 | 142-0701-801 | Cinch Connectivity Solutions |  | RF Connectors / Coaxial Connectors PC END MT JCK GLD .062" BOARD THICK | RoHS Compliant |  | 7 | 3 | 22 | 22 | 54
5 | 534-5000 | 5000 | Keystone Electronics |  | Circuit Board Hardware - PCB TEST POINT RED | RoHS Compliant |  | 1 | 0 | 304 | 0 | 304
6 | 538-22-28-8200 | 22-28-8200 | Molex |  | Headers & Wire Housings 2.54MM BREAKAWAY RA 20 CKT Tin | RoHS Compliant |  | 7 | 0 | 941 | 6 | 587
7 | 538-22-15-2086 | 22-15-2086 | Molex |  | Headers & Wire Housings 8 POS RT ANGLE PCB | RoHS Compliant |  | 1 | 1 | 1 | 1 | 1
8 | 926-LM555CN/NOPB | LM555CN/NOPB | Texas Instruments |  | Timers & Support Products TIMER | RoHS Compliant |  | 2 | 0 | 981 | 1 | 962
9 | 689-MD0100N8-G | MD0100N8-G | Microchip |  | Switch ICs - Various HIGH VOLTAGE PROTECT T/R SWITCH | RoHS Compliant |  | 3 | 1 | 1 | 5 | 5
10 | 595-OPA625IDBVT | OPA625IDBVT | Texas Instruments |  | Precision Amplifiers SAR ADC Driver w/Power Scaling | RoHS Compliant | New Product | 1 | 2 | 56 | 2 | 56
11 | 619-350-00001 | 350-00001 | Parallax |  | Standard LEDs - Through Hole Green LED | RoHS Compliant |  | 1 | 0 | 462 | 0 | 462
12 | 511-BAT48 | BAT48 | STMicroelectronics |  | Schottky Diodes & Rectifiers 350mA 40 Volt | RoHS Compliant |  | 1 | 0 | 321 | 0 | 321
13 | 512-1N4148 | 1N4148 | Fairchild Semiconductor |  | Diodes - General Purpose | RoHS Compliant |  | 17 | 0 | 18 | 0 | 306
14 | 652-RLB0608-100KL | RLB0608-100KL | Bourns |  | Fixed Inductors 10uH 10% 550mA | RoHS Compliant |  | 1 | 0 | 237 | 0 | 237
15 | 926-LM2940CT-5.0NOPB | LM2940CT-5.0/NOPB | Texas Instruments |  | LDO Voltage Regulators 1A LDO REG | RoHS Compliant |  | 1 | 1 | 45 | 1 | 45
16 | 926-LM1117T-3.3/NOPB | LM1117T-3.3/NOPB | Texas Instruments |  | LDO Voltage Regulators 800MA LDO LINEAR REG | RoHS Compliant |  | 1 | 1 | 32 | 1 | 32
17 | 926-LM2990T-12/NOPB | LM2990T-12/NOPB | Texas Instruments |  | LDO Voltage Regulators NEG LDO REG | RoHS Compliant |  | 1 | 2 | 88 | 2 | 88
18 | 926-LM2990T-5.0/NOPB | LM2990T-5.0/NOPB | Texas Instruments |  | LDO Voltage Regulators NEG LDO REG | RoHS Compliant By Exemption |  | 1 | 2 | 88 | 2 | 88
19 | 992-ARD-NANO30NP | ARD-NANO30NP | Arduino |  | Development Boards & Kits - AVR Arduino Nano 3.1 W/ATMEGA328 NO-PIN | RoHS Compliant |  | 1 | 29 | 3 | 29 | 3
20 | 926-LM2940T-12.0NOPB | LM2940T-12.0/NOPB | Texas Instruments |  | LDO Voltage Regulators 1A LDO REG | RoHS Compliant |  | 1 | 1 | 48 | 1 | 48
21 | 610-2N2222 | 2N2222 | Central Semiconductor |  | Bipolar Transistors - BJT NPN Silicon | RoHS Compliant |  | 8 | 1 | 7 | 10 | 2
22 | 610-2N2907A | 2N2907A | Central Semiconductor |  | Bipolar Transistors - BJT PNP Gen Pur SS | RoHS Compliant |  | 4 | 1 | 7 | 3 | 4
23 | 603-CFR-25JB-52-220R | CFR-25JB-52-220R | Yageo |  | Carbon Film Resistors - Through Hole 1/4W 220 Ohm 5% 250 Volts | RoHS Compliant |  | 1 | 0 | 94 | 0 | 94
24 | 660-MF1/4LCT52R271J | MF1/4LCT52R271J | KOA Speer |  | Metal Film Resistors - Through Hole 1/4 WATT 270 OHM 5% | RoHS Compliant |  | 1 | 0 | 101 | 0 | 101
25 | 660-MF1/4LCT52R331J | MF1/4LCT52R331J | KOA Speer |  | Metal Film Resistors - Through Hole 1/4 WATT 330 OHM 5% | RoHS Compliant |  | 1 | 0 | 101 | 0 | 101
26 | 603-MFR-25FRF521K5 | MFR-25FRF52-1K5 | Yageo |  | Metal Film Resistors - Through Hole 1.5K ohm 1/4W 1% | RoHS Compliant By Exemption |  | 4 | 0 | 94 | 0 | 376
27 | 660-MF1/4LCT52R182G | MF1/4LCT52R182G | KOA Speer |  | Metal Film Resistors - Through Hole 1/4 WATT 1.8K OHM 2% | RoHS Compliant |  | 2 | 0 | 101 | 0 | 202
28 | 660-MF1/4LCT52R222J | MF1/4LCT52R222J | KOA Speer |  | Metal Film Resistors - Through Hole 1/4 WATT 2.2K OHM 5% | RoHS Compliant |  | 2 | 0 | 101 | 0 | 202
29 | 660-MF1/4LCT52R332J | MF1/4LCT52R332J | KOA Speer |  | Metal Film Resistors - Through Hole 1/4 WATT 3.3K OHM 5% | RoHS Compliant |  | 2 | 0 | 101 | 0 | 202
30 | 660-MF1/4LCT52R392J | MF1/4LCT52R392J | KOA Speer |  | Metal Film Resistors - Through Hole 1/4 WATT 3.9K OHM 5% | RoHS Compliant |  | 1 | 0 | 101 | 0 | 101
31 | 660-MF1/4LCT52R123J | MF1/4LCT52R123J | KOA Speer |  | Metal Film Resistors - Through Hole 1/4 WATT 12K OHM 5% | RoHS Compliant |  | 2 | 0 | 101 | 0 | 202
32 | 660-MF1/4LCT52R333J | MF1/4LCT52R333J | KOA Speer |  | Metal Film Resistors - Through Hole 1/4 WATT 33K OHM 5% | RoHS Compliant |  | 1 | 0 | 101 | 0 | 101
33 | 140-REA330M2CBK1320P | REA330M2CBK-1320P | Lelon |  | Aluminium Electrolytic Capacitors - Leaded 160V 33uF 20% 12.5x20mm | RoHS Compliant | Factory Special Order | 1 | 0 | 356 | 0 | 356
34 | 647-UVR2C4R7MED1TD | UVR2C4R7MED1TD | Nichicon |  | Aluminium Electrolytic Capacitors - Leaded 4.7uF 160V 85c | RoHS Compliant |  | 1 | 0 | 255 | 0 | 255
35 | 647-UVR1E100MDD6 | UVR1E100MDD6 | Nichicon |  | Aluminium Electrolytic Capacitors - Leaded 10uF 25 Volts 20% | RoHS Compliant | New Product | 3 | 0 | 264 | 0 | 792
36 | 647-UMA1E4R7MDD | UMA1E4R7MDD | Nichicon |  | Aluminium Electrolytic Capacitors - Leaded 25volts 4.7uF 4x5 20% 1.5LS | RoHS Compliant |  | 11 | 0 | 9 | 0 | 99
37 | 647-UVR1E470MDD6 | UVR1E470MDD6 | Nichicon |  | Aluminium Electrolytic Capacitors - Leaded 47uF 25 Volts 20% | RoHS Compliant | New Product | 8 | 0 | 174 | 1 | 392
38 | 598-107CKS035M | 107CKS035M | Cornell Dubilier |  | Aluminium Electrolytic Capacitors - Leaded 100uF 35V 20% | RoHS Compliant | New Product | 2 | 0 | 226 | 0 | 452
39 | 598-227CKS025MGM | 227CKS025MGM | Cornell Dubilier |  | Aluminium Electrolytic Capacitors - Leaded 220uF 25 Volts 20% LYTICS/IC | RoHS Compliant | New At Mouser | 1 | 0 | 94 | 0 | 94
40 | 594-S100K25SL0N63L6R | S100K25SL0N63L6R | Vishay |  | Ceramic Disc Capacitors Radial 10pF 1Kvolts Z5P +/-10% | RoHS Compliant By Exemption |  | 1 | 0 | 141 | 0 | 141
41 | 581-SR151C102KAA | SR151C102KAA | AVX |  | Multilayer Ceramic Capacitors MLCC - Leaded 100volts 1000pF 10% X7R | RoHS Compliant |  | 2 | 0 | 94 | 0 | 188
42 | 594-K103K15X7RF5UH5 | K103K15X7RF5UH5 | Vishay |  | Multilayer Ceramic Capacitors MLCC - Leaded .01uF 50volts 10% 5.0mm X7R | RoHS Compliant |  | 2 | 0 | 94 | 0 | 188
43 | 75-1C10Z5U473M050B | 1C10Z5U473M050B | Vishay |  | Multilayer Ceramic Capacitors MLCC - Leaded 47000pF 50V Z5U 20% 2.5mm LS | RoHS Compliant |  | 2 | 0 | 94 | 0 | 188
44 | 21RZ310-RC | 21RZ310-RC | Xicon |  | Multilayer Ceramic Capacitors MLCC - Leaded .1uF 50volts Z5U 20% 2.5mm L/S | RoHS Compliant |  | 2 | 0 | 86 | 0 | 172
45 | 71-CCF071K00JKE36 | CCF071K00JKE36 | Vishay |  | Metal Film Resistors - Through Hole 1/4watt 1Kohms 5% Rated to 1/2watt | RoHS Compliant |  | 1 | 0 | 94 | 0 | 94
46 | 598-226KXM063M |  |  |  | condo 22uF |  |  | 1 | 0 | 66 | 0 | 66
47 | 603-CFR-25JR-52-680R |  |  |  | Resistance 680 Ohm |  |  | 2 | 0 | 984 | 0 | 1968
By submitting your order you agree to these terms and conditions. |  |  |  |  |  |  |  |  | Merchandise Total: | 238 | 6548
Prices are reflected at the date and time shown. |  |  |  |  |  |  |  |  | Delivery Charge: | 0 | 00 €
 |  |  |  |  |  |  |  |  | Back-order Delivery: | 0 | 00 €

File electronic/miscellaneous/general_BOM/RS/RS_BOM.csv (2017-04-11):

Type | Reference | Quantity | Unitariy price | Total price
dongle wifi | 760-3621 | 1 | 12,09 | 12,09
matrix board | 528-0661 | 1 | 6,9 | 6,9
wifi dongle | 760-3621 | 1 | 12,09 | 12,09
RedPitaya | 127-1084 | 1 | 258,7 | 258,7
sma cable | 914-0359 | 5 | 6,52 | 32,6 | often out of stock…
 |  |  |  | 0

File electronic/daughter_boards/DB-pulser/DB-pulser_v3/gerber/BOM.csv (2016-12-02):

Reference | Value | Footprint | Datasheet | Caracteristic | Manufacturer | Ref Manufacturer
R2 | 22 | Echopen:Resistor_TH_common |  | 1/4W 5% | Yageo | CFR-25JR-52-22R
C1 | 100p | Echopen:C_TH_common |  | 25V 10% | Xicon | 140-50N5-101J-TB-RC
C5 | 220p | Echopen:C_TH_common |  | 25V 10% | Vishay | K221K15X7RF5TL2
D1 | BAT48 | Echopen:D_TH_common |  | NA | STMicroelectronics | BAT48
D3 | 1N4148 | Echopen:D_TH_common |  | NA | Fairchild Semiconductor | 1N4148
R6 | 100k | Echopen:Resistor_TH_common |  | 1/4W 10% | Vishay | CCF07100KJKE36
R1 | 1k | Echopen:Resistor_TH_common |  | 1/4W 5% | Yageo | MFR-25FRF52-1K
C2 | 100n | Echopen:C_TH_common |  | 25V 20% | Xicon | 21RZ310-RC
C4 | 100n | Echopen:C_TH_common |  | 25V 20% | Xicon | 21RZ310-RC
D5 | 1N4746 | Echopen:D_TH_common |  | Zener 18V | Vishay | 1N4746A-TR
D2 | 1N4746 | Echopen:D_TH_common |  | Zener 18V | Vishay | 1N4746A-TR
R5 | 1M | Echopen:Resistor_TH_common |  | 1/4W 5% | Yageo | MFR-25FBF52-1M
R3 | 1M | Echopen:Resistor_TH_common |  | 1/4W 5% | Yageo | MFR-25FBF52-1M
Q7 | IRF9610 | Echopen:TO-220_TH_common |  | NA | Vishay | IRF9610PBF
Q8 | IRF610 | Echopen:TO-220_TH_common |  | NA | Vishay | IRF610PBF
P1 | CONN_01X19 | Echopen:Header_pin_angled_1x19 |  | NA | Molex | 22-28-8192
P2 | CONN_01X02 | Echopen:Socket_1x02 |  | angled socket 1*02 | Molex | 22-15-2026
P4 | CONN_01X02 | Echopen:Socket_1x02 |  | angled socket 1*02 | Molex | 22-15-2026
P5 | SMA | Echopen:SMA |  | NA | Johnson / Cinch Connectivity Solutions | 142-0701-801
C3 | 33u | Echopen:CP_TH_common |  | 150V 20% | Lelon | REA330M2CBK-1320P
Q1 | 2N2907 | Echopen:TO-18_TH_common |  | NA | Central Semiconductor | 2N2907A
Q2 | 2N2222 | Echopen:TO-18_TH_common |  | NA | Central Semiconductor | 2N2222
Q3 | 2N2222 | Echopen:TO-18_TH_common |  | NA | Central Semiconductor | 2N2222
Q4 | 2N2907 | Echopen:TO-18_TH_common |  | NA | Central Semiconductor | 2N2907A
Q5 | 2N2222 | Echopen:TO-18_TH_common |  | NA | Central Semiconductor | 2N2222
Q6 | 2N2907 | Echopen:TO-18_TH_common |  | NA | Central Semiconductor | 2N2907A
P6 | SMA | Echopen:SMA |  | NA | Johnson / Cinch Connectivity Solutions | 142-0701-801
P7 | CONN_01X02 | Echopen:Socket_1x02 |  | angle socket 1*02 | Molex | 22-15-2026
P8 | SMA | Echopen:SMA |  | NA | Johnson / Cinch Connectivity Solutions | 142-0701-801

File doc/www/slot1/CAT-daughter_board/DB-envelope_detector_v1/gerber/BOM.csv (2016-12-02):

Reference | Value | Footprint | Datasheet | Caracteristic | Manufacturer | Ref Manufacturer
D1 | 1N60 | Echopen:D_TH_common |  | Germanium diode | NA | 1N60 DO-7
R1 | 3.9k | Echopen:Resistor_TH_common |  | 1/4W 5% | KOA speer | MF1/4LCT52R392J
C1 | 10p | Echopen:C_TH_common |  | 25V 10% | Xicon | 140-50N5-100J-TB-RC
P1 | CONN_01X19 | Echopen:Header_pin_angled_1x19 |  | angled pin header 1*19 | Molex | 22-28-8192

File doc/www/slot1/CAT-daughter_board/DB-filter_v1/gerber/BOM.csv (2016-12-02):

Reference | Value | Footprint | Datasheet | Caracteristic | Manufacturer | Ref Manufacturer
C1 | 1n | Echopen:C_TH_common |  | 25V 10% | AVX | SR151C102KAA
L1 | 10u | Inductors:INDUCTOR_V |  | 10% 550mA | Bourns | RLB0608-100KL
R1 | 330 | Echopen:Resistor_TH_common |  | 1/4W 5% | KOA speer | MF1/4LCT52R331J
P1 | CONN_01X19 | Echopen:Header_pin_angled_1x19 |  | angled pin header 1*19 | Molex | 22-28-8192

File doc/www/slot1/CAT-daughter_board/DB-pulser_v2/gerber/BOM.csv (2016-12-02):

Reference | Value | Footprint | Datasheet | Caracteristic | Manufacturer | Ref Manufacturer
P1 | CONN_01X19 | Echopen:Header_pin_1x19 |  | Angled pin header 1*19 | Molex | 22-28-8192
P3 | CONN_01X08 | Echopen:Socket_Strip_Straight_1x08 |  | angled socket 1*08 | Molex | 22-15-2086
P4 | SMA | Echopen:SMA |  | NA | Johnson / Cinch Connectivity Solutions | 142-0701-801
P2 | CONN_01X02 | Echopen:Socket_1x02 |  | angled socket 1*02 | Molex | 22-15-2026
P5 | CONN_01X02 | Echopen:Socket_1x02 |  | angled socket 1*02 | Molex | 22-15-2026
P7 | SMA | Echopen:SMA |  | NA | Johnson / Cinch Connectivity Solutions | 142-0701-801
P6 | CONN_01X02 | Echopen:Socket_1x02 |  | angled socket 1*02 | Molex | 22-15-2026
P8 | SMA | Echopen:SMA |  | NA | Johnson / Cinch Connectivity Solutions | 142-0701-801
33u(150V) | CP | Echopen:CP_TH_common |  | 150V 20% | Lelon | REA330M2CBK-1320P

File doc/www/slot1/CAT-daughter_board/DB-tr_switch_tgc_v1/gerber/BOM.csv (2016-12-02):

Reference | Value | Footprint | Datasheet | Caracteristic | Manufacturer | Ref Manufacturer
U1 | MD0100 | Echopen:SOT89-3_(MD0100) |  | NA | Microchip Technology | MD0100N8-G
D1 | 1N4148 | Echopen:D_TH_common |  | high speed diode | Fairchild Semiconductor | 1N4148
D2 | 1N4148 | Echopen:D_TH_common |  | high speed diode | Fairchild Semiconductor | 1N4148
P1 | CONN_01X19 | Echopen:Header_pin_angled_1x19 |  | angled pin 1*19 | Molex | 22-28-8192
P3 | SMA | Echopen:SMA |  | NA | Johnson / Cinch Connectivity Solutions | 142-0701-801
P2 | CONN_01X02 | Echopen:Socket_1x02 |  | angled socket 1*02 | Molex | 22-15-2026
C1 | 1n | Echopen:C_TH_common |  | 25V 10% | AVX | SR151C102KAA
R1 | 220 | Echopen:Resistor_TH_common |  | 1/4W 5% | Yageo | CFR-25JB-52-220R
AOP1 | OPA625 | Echopen:SOT-23-6_Handsoldering(OPA625) |  | high speed OPA | TI | OPA625IDBVT
P8 | SMA | Echopen:SMA |  | NA | Johnson / Cinch Connectivity Solutions | 142-0701-801
P6 | CONN_01X02 | Echopen:Socket_1x02 |  | angled socket 1*02 | Molex | 22-15-2026
P9 | SMA | Echopen:SMA |  | NA | Johnson / Cinch Connectivity Solutions | 142-0701-801
P7 | CONN_01X02 | Echopen:Socket_1x02
W1 | TEST_1P | Echopen:Test_Point |  | test point | Keystone Electronics | 5000
W2 | TEST_1P | Echopen:Test_Point |  | test point | Keystone Electronics | 5000

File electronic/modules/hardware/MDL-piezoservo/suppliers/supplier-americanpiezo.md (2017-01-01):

### Info [](@description supplier source file)

* Name: American Piezo (APC)
* Site: americanpiezo.com
* Contact: sales@americanpiezo.com, jzahnd@americanpiezo.com

### Status

* Deja contactes en 2015
* @contacted, @followup on 2/1/16

### Notes

#### December 2015

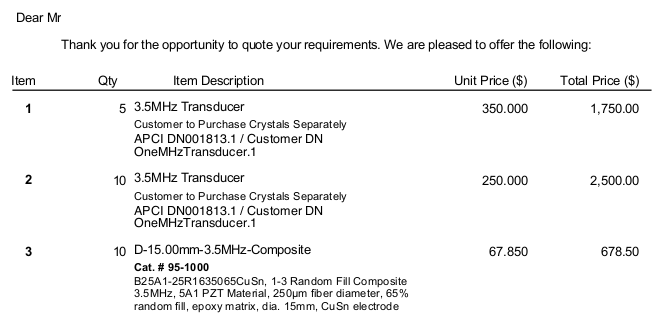
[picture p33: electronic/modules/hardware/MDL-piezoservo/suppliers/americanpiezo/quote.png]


* From Jeff: Crystal @67$, Casing at 250$. The minimum order for Crystals is Qty 10.

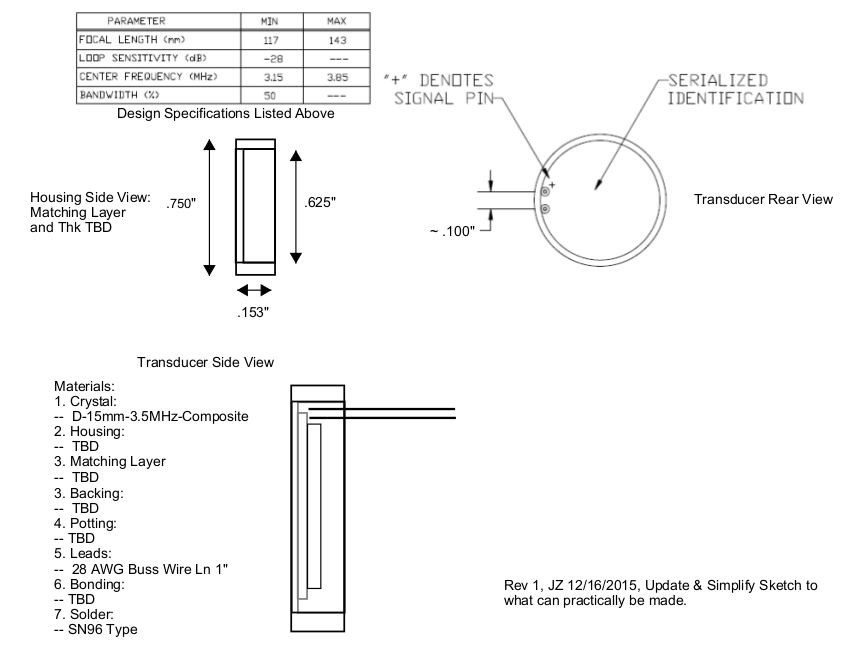
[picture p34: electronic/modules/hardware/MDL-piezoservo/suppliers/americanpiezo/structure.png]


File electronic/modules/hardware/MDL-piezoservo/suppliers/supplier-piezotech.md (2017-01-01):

### Info [](@description supplier source file)

* Name: PiezoTechnologies
* Site: http://www.piezotechnologies.com/documents/120710-material-data-sheet.aspx
* Contact: MSSIndyMarketing@meggitt.com

### Status

* Deja contactes en 2015 
* Retour 2/1/16: need the [query sheet](/electronic/modules/hardware/MDL-piezoservo/suppliers/meggitt/query.pdf)

### Notes

#### Contacts

* George Gabuzda
    * Director of Sales and Marketing
    * Piezo Technologies
    * 317-403-9121
    * George.gabuzda@meggitt.com
* "Molz, Eric (US - MSSIN)" <Eric.Molz@meggitt.com>,
* "Gilbert, Jeff (US - MSSIN)" <jeff.gilbert@meggitt.com>

#### Sheet

* To provode more details on the required piezo : [Download](/electronic/modules/hardware/MDL-piezoservo/suppliers/meggitt/query.pdf)

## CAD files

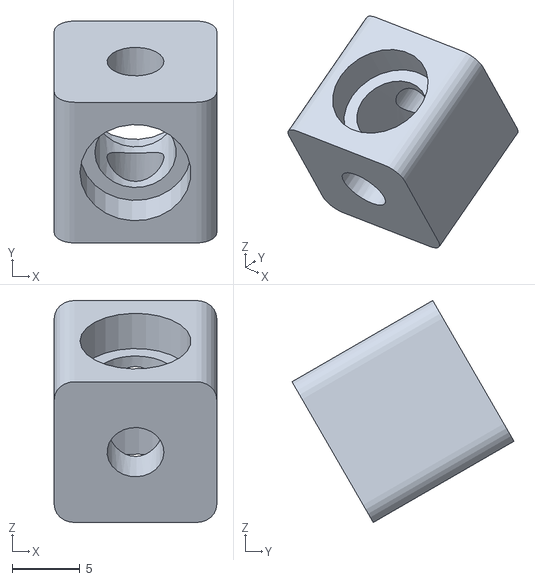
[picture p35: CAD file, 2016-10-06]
modules/MDL-mechanism_cc_motor_mono/trash/2015-11-29 sonde_complete_v3.2_noix.stl
12.0 x 16.4 x 16.4

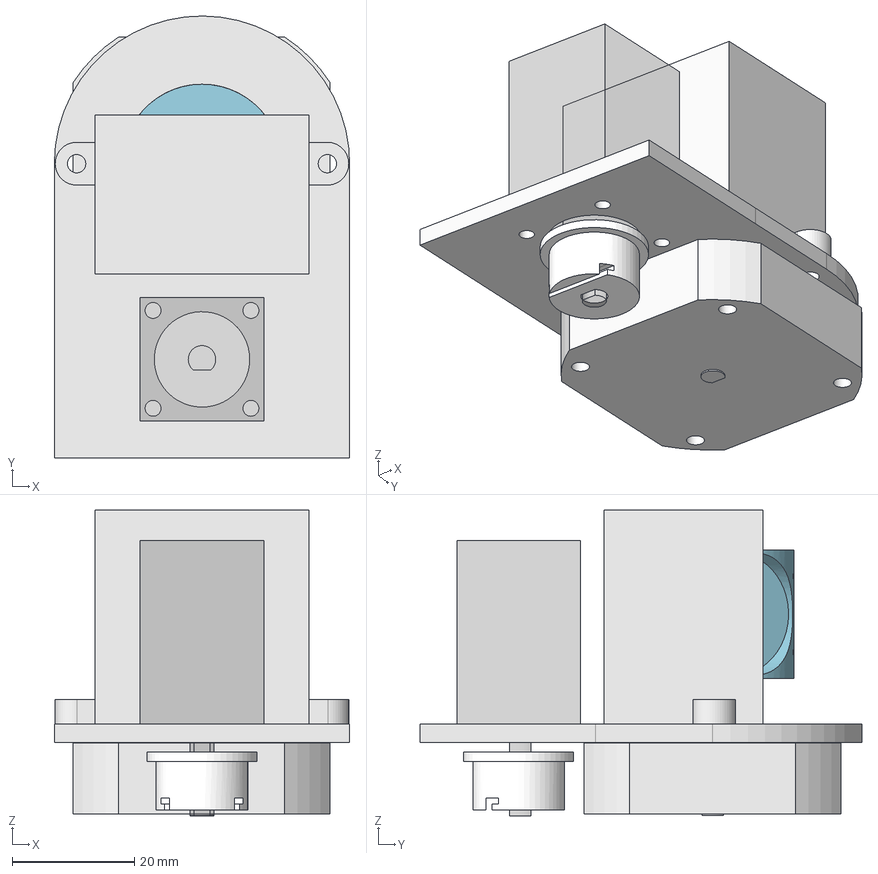
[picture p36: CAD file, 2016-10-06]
modules/MDL-mechanism_stepper_timing_belt/src/probe_mod_TFS_assembly.FCStd
48.3 x 72.3 x 50.0 mm
frame
motor
drum_shaft
drum
pulley_01
pulley_02
capsule_01
motor_pancake_01

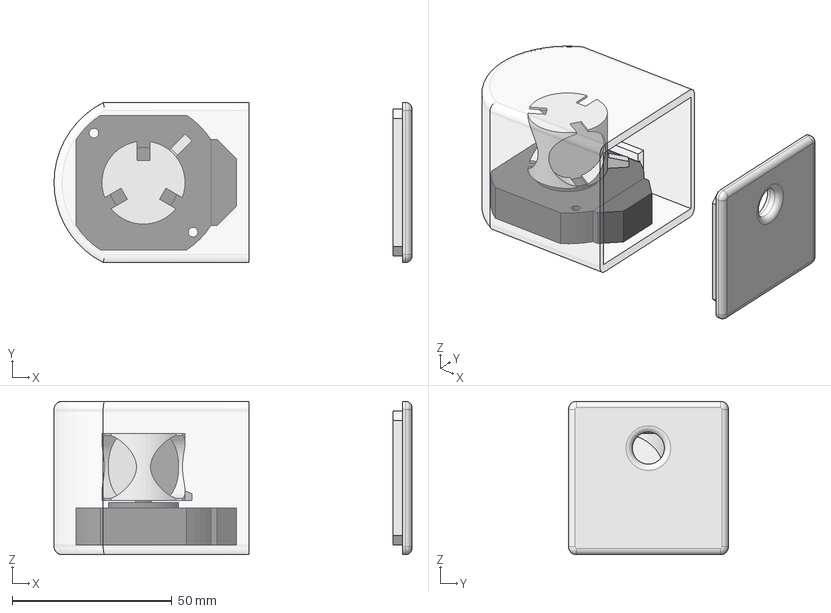
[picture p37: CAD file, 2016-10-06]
modules/MDL-mechanism_stepper_tri_palm/src/probe_mod_TFS_assembly_v2.FCStd
112.0 x 50.1 x 48.0 mm
motor_pancake_01
drum_pnck_01

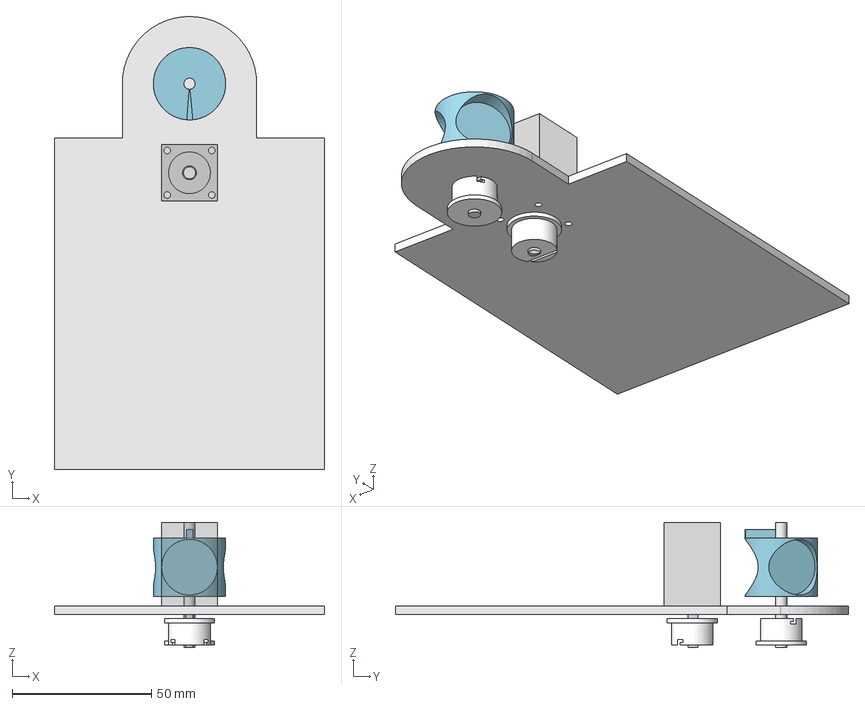
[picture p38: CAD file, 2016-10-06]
modules/MDL-mechanism_stepper_tri_water/trash/assembly_sonde_mod_S.FCStd
97.0 x 162.7 x 45.1 mm
platine_01
mot_pp_1204_01
axe_4_01
tambour_01
poulie_01
poulie_02

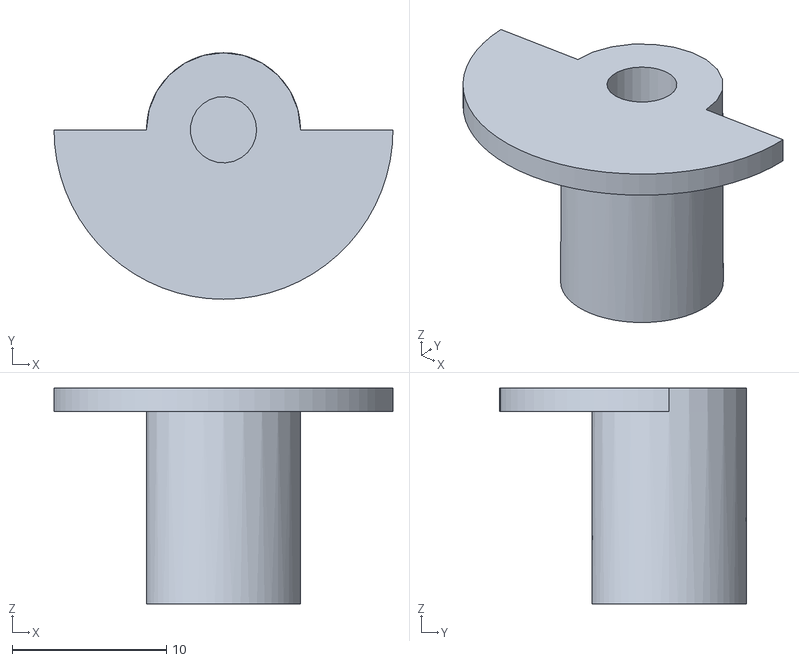
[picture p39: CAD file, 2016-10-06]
modules/MDL-mechanism_cc_motor_mono/trash/2015-11-29 sonde_complete_v3.3_manchon.stl
22.0 x 16.0 x 14.0

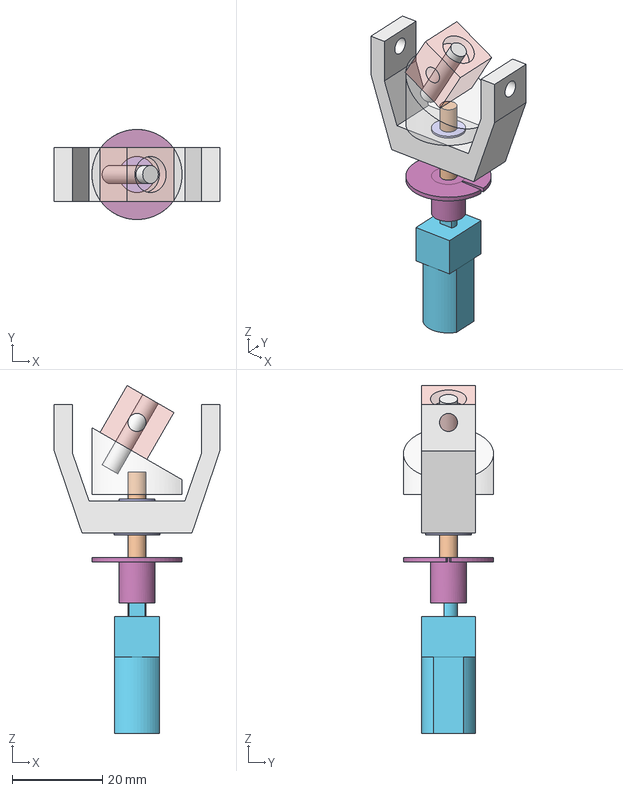
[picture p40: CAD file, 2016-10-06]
modules/MDL-mechanism_cc_motor_mono/trash/2015-11-29 sonde_complete_v2.FCStd
36.7 x 20.0 x 77.2 mm
Axe
Moteur
Manchon
Roulement
Joint
Oscillateur
Axe 30
Tambour

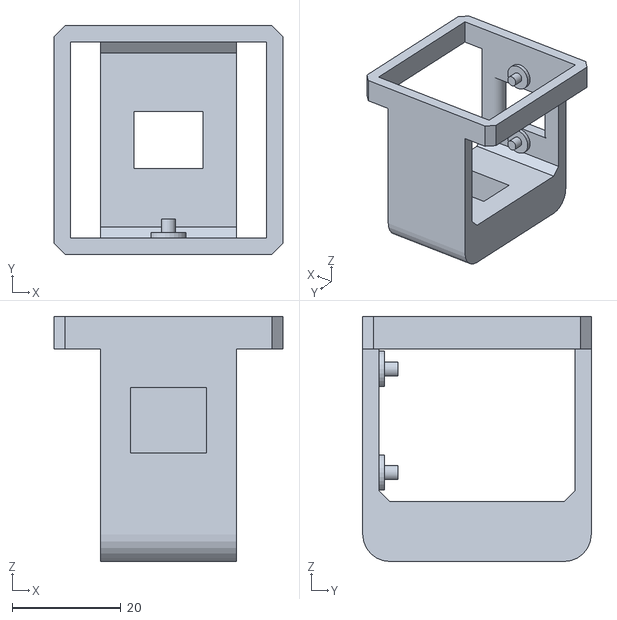
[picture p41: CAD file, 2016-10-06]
modules/MDL-mechanism_cc_motor_mono/trash/2015-11-29 sonde_complete_v3.3_support.stl
42.0 x 42.0 x 45.0

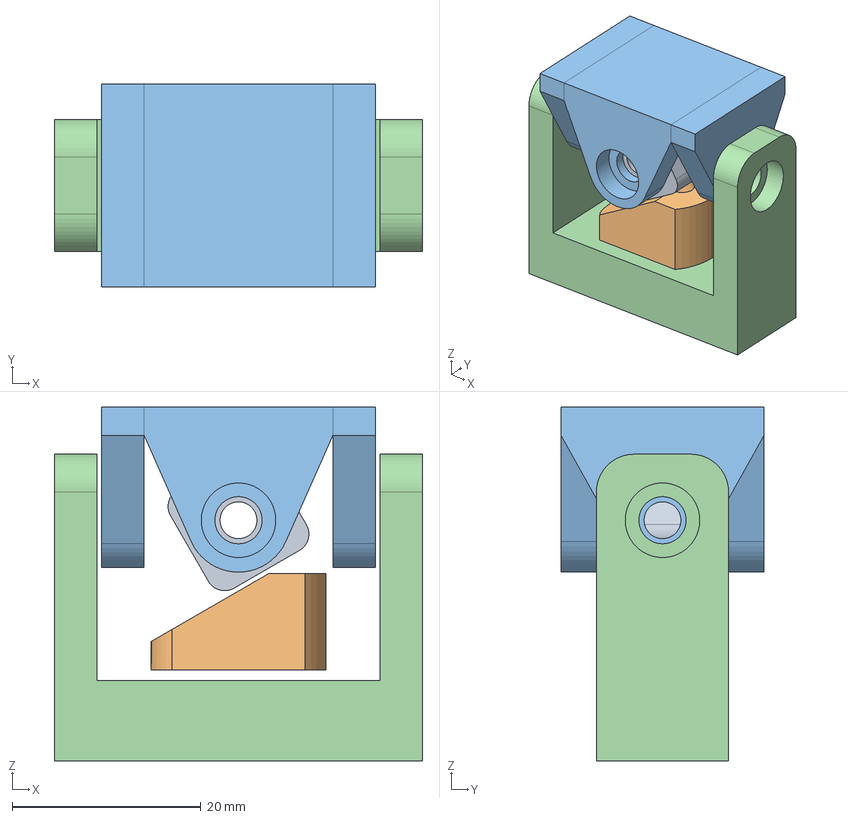
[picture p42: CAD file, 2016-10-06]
modules/MDL-mechanism_cc_motor_mono/trash/2015-11-29 sonde_complete_v3.0.FCStd
39.0 x 21.5 x 37.5 mm

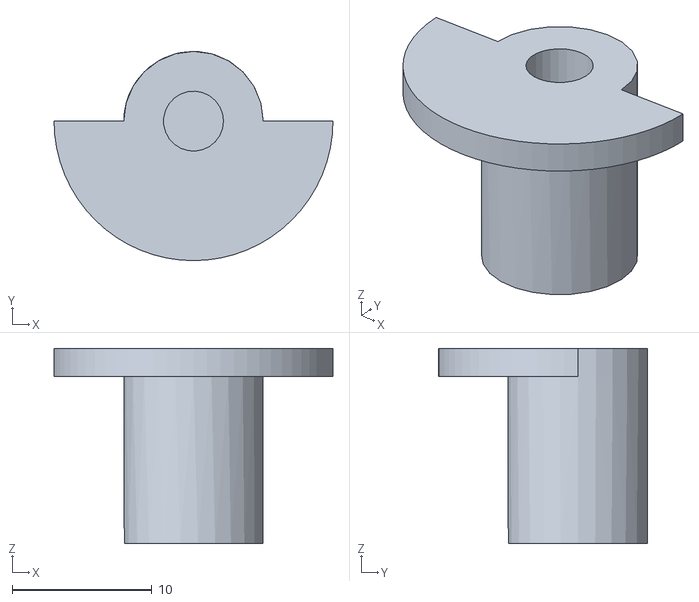
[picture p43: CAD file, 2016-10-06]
modules/MDL-mechanism_cc_motor_mono/trash/2015-11-29 sonde_complete_v3.2_manchon.stl
20.0 x 15.0 x 14.0

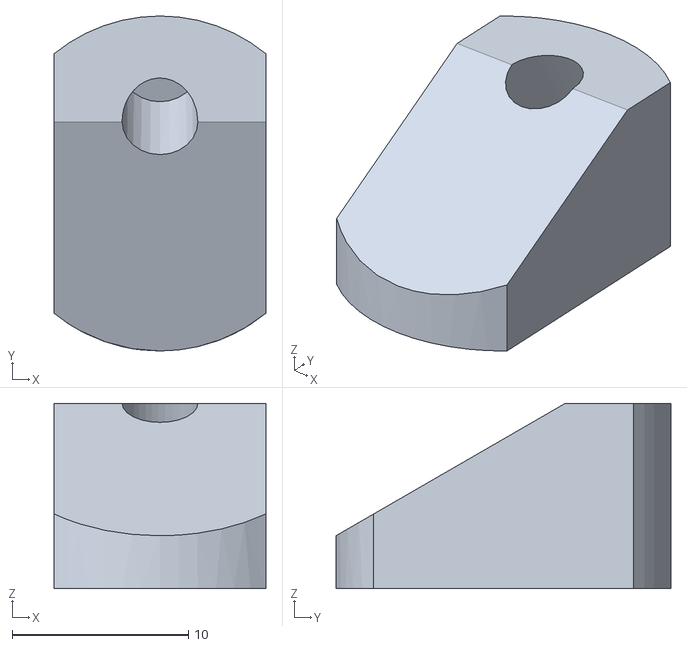
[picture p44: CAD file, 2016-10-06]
modules/MDL-mechanism_cc_motor_mono/trash/2015-11-29 sonde_complete_v3.2_tambour.stl
12.0 x 19.0 x 10.5

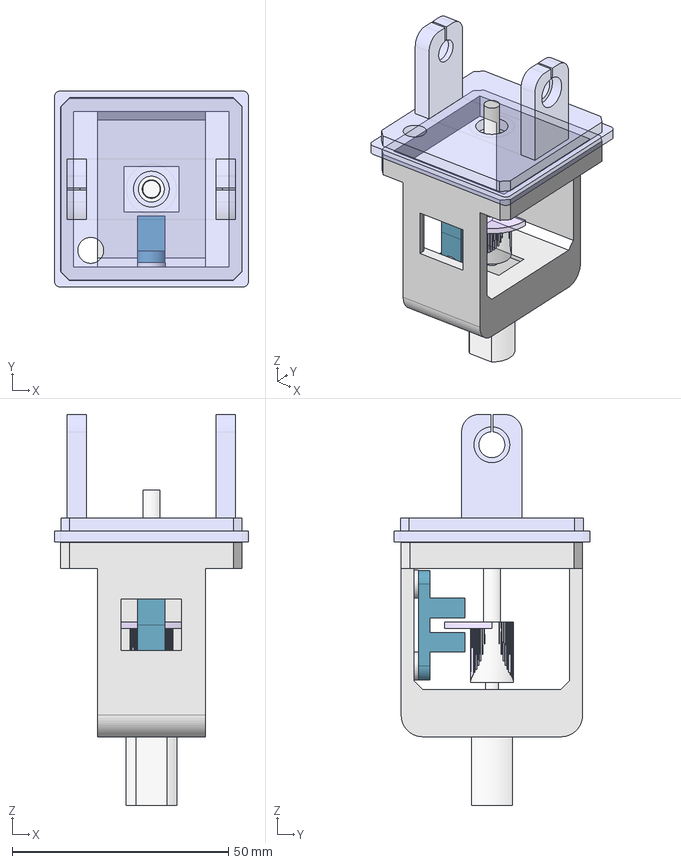
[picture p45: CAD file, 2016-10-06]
modules/MDL-mechanism_cc_motor_mono/trash/2015-11-29 sonde_complete_v3.3.FCStd
45.0 x 45.4 x 90.5 mm

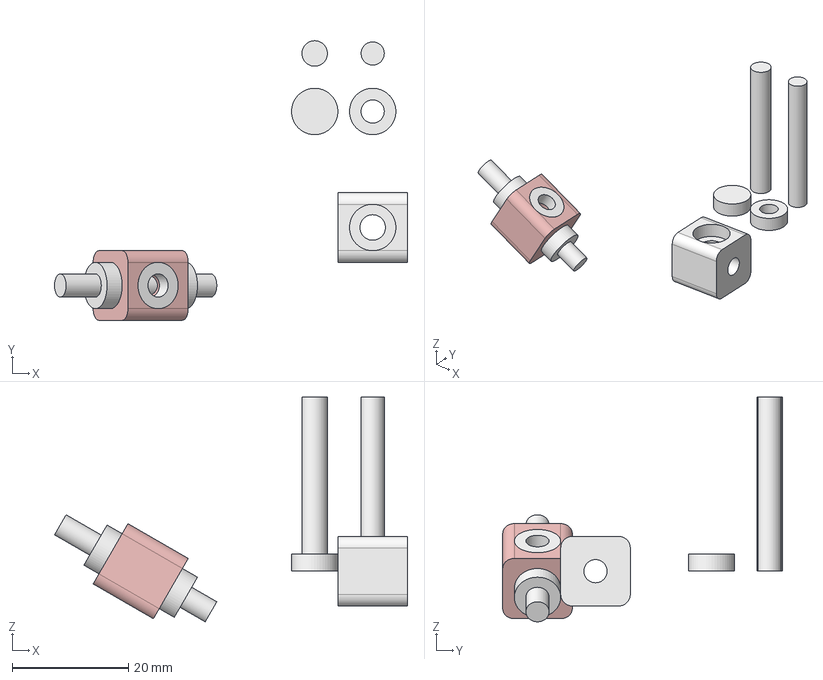
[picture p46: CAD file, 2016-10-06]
modules/MDL-mechanism_cc_motor_mono/trash/test assemblage v1.FCStd
60.9 x 48.2 x 38.7 mm
Axe_4
Roulement_4
Logement_4
Axe_4_passage
Clone of Noix
Clone of Axe_005
Clone of Roulement_4
Clone of Roulement_005
Clone of Roulement_006
Clone of Roulement_007

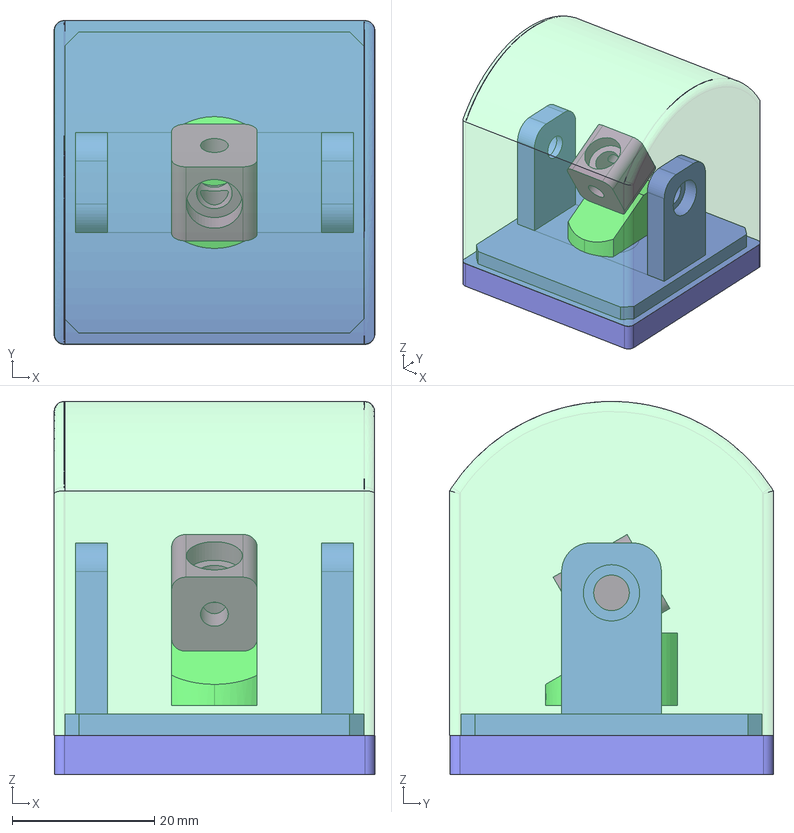
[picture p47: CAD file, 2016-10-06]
modules/MDL-mechanism_cc_motor_mono/trash/2015-11-29 sonde_complete_v3.1.FCStd
45.0 x 45.5 x 52.4 mm

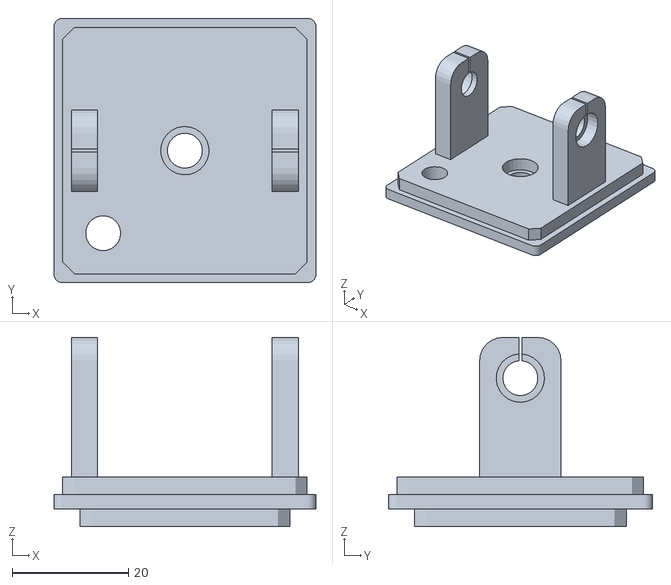
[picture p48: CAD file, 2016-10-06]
modules/MDL-mechanism_cc_motor_mono/trash/2015-11-29 sonde_complete_v3.2_etrier.stl
45.0 x 45.4 x 32.5

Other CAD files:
modules/MDL-mechanism_cc_motor_mono/trash/2015-11-29 sonde_complete_v3.2.FCStd
modules/MDL-mechanism_cc_motor_mono/trash/2015-11-29 sonde_complete_v3.2_plateau.stl
modules/MDL-mechanism_cc_motor_mono/trash/2015-11-29 sonde_complete_v1.FCStd
mecanic/modules/MDL-motor_support/src/MDL-motor_support.igs
electronic/modules/hardware/legacy/MDL-mechanism_cc_motor_mono/build/mechanism_adaptateur.stl
electronic/modules/hardware/legacy/MDL-mechanism_cc_motor_mono/build/mechanism_capot.stl
electronic/modules/hardware/legacy/MDL-mechanism_cc_motor_mono/build/mechanism_cloche.stl
electronic/modules/hardware/legacy/MDL-mechanism_cc_motor_mono/build/mechanism_griffe_imasonic.stl
electronic/modules/hardware/legacy/MDL-mechanism_cc_motor_mono/build/mechanism_griffe_laser.stl
electronic/modules/hardware/legacy/MDL-mechanism_cc_motor_mono/build/mechanism_griffe_trancducteur1.stl
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

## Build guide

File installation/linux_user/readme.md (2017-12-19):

## Software installation

In this repo there is two bash script:  
 ./echopen_light.sh that install minimal configuration if you just want to use the kit without modifying the firmware of the RedPitaya. This bash file install vim, sshpass, gnuplot and kicad. We need gnuplot when using the C software display tool on linux. Kicad is an open-source software to make electronic.   
 ./echopen_full.sh, that install all te tools even the ones for compiling C scripts of the RedPitaya.

The tool that will be installed are:  
 sshpass  
 kicad  
 ...

To install one of this files just type the command line:  
`sh echopen_light.sh`  
or  
`sh echopen_full.sh`

You also have to install arduino IDE, follow the instruction on their [website](https://www.arduino.cc/en/Guide/Linux).

### kicad

To edit a Bom, on linux we have install xsltproc with the sh file previously. Then in the schematic tool, click on the BOM icon, select Add Plugin, the plugins can be found in:

    /usr/lib/kicad/plugins

and select bom2csv.xsl. To edit a csv file you have to edit the command by changing "%O" to "%O.csv": 

    xsltproc -o "%O" "/usr/lib/kicad/plugins/bom2csv.xsl" "%I"

become:

    xsltproc -o "%O.csv" "/usr/lib/kicad/plugins/bom2csv.xsl" "%I"

to improve the BOM output one can for example use the tool in http://www.hashdefineelectronics.com/kicad-bom-wizard/

To add a librairy with a relative path go to Preferences/Component librairies then in User defined search path add the folder you want to add and select use relative path. In Component library files add the librairy, by doing this, the library is added with an absolute path, to access a relative path edit the .rpo filewith a text editor, at the end of the file you will find the librairy you added with the absolute path, clear all the path and keep only the name of the labrairy.

When you to make a PCB for the first time, go to your Eschema file and click on the CvPcb icon. In the new window, click on the Preferences menu and select Footprint Librairies. In the new window delete all the librairies that are listed (there is not the librairies install on the computer and you will have error when you will want to associate footprint) then click on Append with wizard. Now you use the online librairies. Now you can associate the footprints with the component, enjoy.

Some interesting tutorial about kicad can be found on:

https://www.wayneandlayne.com/blog/category/kicad-tutorials/

## Prepare the RedPitaya

RedPitaya board need a 5V, 2A supply for the RedPitya.

Before turning on the RedPitaya, please copy the [old OS server files](../../electronic/modules/hardware/MDL-redpitaya/OS/server/) (../../modules/electronic/hardware/MDL-redpitaya/OS/server/) into a blank micro-SD card. We use the old RedPitaya OS (0.92) because we have found a bug with the trigger C function with the new OS.

You must also plug a WIFI dongle (such as [edimax EW_7811Un dongle](http://www.edimax.fr/edimax/merchandise/merchandise_detail/data/edimax/fr/wireless_adapters_n150/ew-7811un/)). With the files you have copy into the SD card, the RedPitaya act as an access point, the WIFI name is **redpitaya** and the pass is also **redpitaya**. It's IP adress is 192.168.128.3 and pass and ID are both root. So to access the RedPitaya *via* ssh one must enter the folowing command lines:  
`ssh root@192.168.128.3`  
`root`

## Built the kit and download the android app

All step to built our kit can be found in our [prototyping gitbook section production guide](https://echopen.gitbooks.io/echopen_prototyping/content/stable/guide_hardware.html).

To download on your smartphone, you must follow the instructions given in the [android app github](https://github.com/echopen/PRJ-medtec_androidapp). This procedure is quite long for the moment. A simple and quick way to download the app on your smartphone will be done soon.

## How to launch the acquisition

* When the kit is built, connect a 18 V power supply to it. Not power on the supply for the moment.

* Go to [software folder](../../electronic/modules/software) and select the folder corresponding to your configuration, the latest one is actually the  [aquarium kit folder](../../electronic/modules/software/CFG-aquarium_kit).

* Lauch arduino IDE and check that the right arduino board is selected by clicquing on tools:  
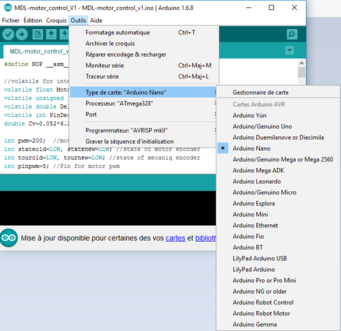
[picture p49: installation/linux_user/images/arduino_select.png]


* Open the arduino file (./arduino/MDL-pulser_v2.ino file) and push it in the arduino nano:  
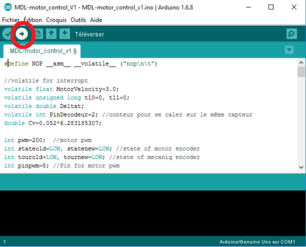
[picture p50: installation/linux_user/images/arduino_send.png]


* Power up your RedPitaya and connect your computer on redpitaya WIFI network, password is redpitaya.

* Go to the RedPitaya repository, for the latest version it is this [repo](../../electronic/modules/software/CFG-aquarium_kit/redpitaya). Now you can either compile the code if you want to change the settings or only send the precompile code to the RedPitaya.

    * If you want to compile the code by yourself, you must have use the ./echopen_full.sh bash file. Change the file ./srcbin/probe.c to use the settings you want, and then run the ./run.sh bash file. This bash file will compile the code, send it the RedPitaya (in /root) and connect your computer to the RedPitaya *via* ssh in the /root forlder.

    * If you just want the use the default code, use ./default_probe file (you may have to change the permission so use chmod) enter on the terminal:  
`chmod 777 default_probe`  
`scp ./default_probe root@192.168.128.3:/tmp/`  
`ssh root@192.168.128.3`  
`root`  

* At this step, the kit is still not power up (if you power it up, you will hear the motor whistle, turn it off). Launch the code on the Redpitaya (enter ./probe or ./default_probe on you terminal) and when it write 'buffer length = 1689' (1689 is for the default_probe, if you have changed the settings, it may be another number) kill it by pressing CTRL+C. Now you can power up the kit (the motor will not whistle like this). We recommand to proceed like this because if not, the motor may consume a lot of power and have a short-circuit behavior.

* Launch once again the code (by entering ./default_probe on your terminal). The motor will turn till it comes on the mechanical stop at knock on it (don't worry it's normal). Then it will turn in the other side to reach the beginning of the sweeping zone and make the sweeping movement.

* The default settings are:
    * beginning of measurement 80 mm,
    * end of measurement 160 mm,
    * sampling rate 15.625 Msps,
    * angle of the sector 60°,
    * speed of the motor 3 tour per second,
    * amplification command at beginning of measurement 0.1 V (0.3 dB of amplification),
    * amplification at end of measurement 1 V (43.5 dB of amplification).

* When you want to stop press CTRL+C, to quit the ssh connection just enter exit in your terminal.

## Display

### Android app

Connect your smartphone to the redpitaya wireless (pass: redpitaya) and launch the echOpen app. And it's done, the echographic image must appear on your smartphone.

### Computer display (for linux only)

One can also use the C software provided in ./src repo. This softs are based on [gnuplot_i](http://ndevilla.free.fr/gnuplot/) tool, tuned for our uses. All the sources are provided here so one can modify them if desire.

probe_mode_A display line by line measurement such as an oscilloscope. probe_mode_B display the full image on gray scale such as an echographic machin, except there is no scan conversion (image display in a rectangle).

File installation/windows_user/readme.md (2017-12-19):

## Softwares needed

Please install these softwares:

* [putty](http://www.chiark.greenend.org.uk/~sgtatham/putty/download.html)
* [WinSCP](https://winscp.net/eng/download.php)
* [arduino IDE](https://www.arduino.cc/en/Main/Software)
* [kicad v4.0.4](http://kicad-pcb.org/download/windows/) (if you want to access to the electronic schematics and PCB design)

## Prepare the RedPitaya

RedPitaya board need a 5V, 2A supply for the RedPitya.

Before turning on the RedPitaya, please copy the [old OS server files](../../electronic/modules/hardware/MDL-redpitaya/OS/server/) (../../modules/electronic/hardware/MDL-redpitaya/OS/server/) into a blank micro-SD card. We use the old RedPitaya OS (0.92) because we have found a bug with the trigger C function with the new OS.

You must also plug a WIFI dongle (such as [edimax EW_7811Un dongle](http://www.edimax.fr/edimax/merchandise/merchandise_detail/data/edimax/fr/wireless_adapters_n150/ew-7811un/)). With the files you have copy into the SD card, the RedPitaya act as an access point, the WIFI name is **redpitaya** and the pass is also **redpitaya**. It's IP adress is 192.168.128.3, pass and ID are both root.

## Built the kit and download the android app

All step to built our kit can be found in our [prototyping gitbook section production guide](https://echopen.gitbooks.io/echopen_prototyping/content/stable/guide_hardware.html).

To download on your smartphone, you must follow the instructions given in the [android app github](https://github.com/echopen/PRJ-medtec_androidapp). This procedure is quite long for the moment. A simple and quick way to download the app on your smartphone will be done soon.

## How to launch the acquisition

In this section, we explain how to launch the latest version of our kit.

* When the kit is built, connect a 18 V power supply to it. Not power on the supply for the moment.

* Lauch arduino IDE and check that the right arduino board is selected by clicquing on tools:  


* Open /PRJ-medtec_kit/electronic/modules/software/CFG-aquarium_kit/arduino/MDL-pulser_v2/MDL-motor_control_v2.ino and send it in the arduino nano:  


* Power up your RedPitaya and connect your computer on redpitaya WIFI network, password is redpitaya.

* Open WinSCP and connect it to the RedPitaya, IP: 192.168.128.3, ID: root, pass: root:  
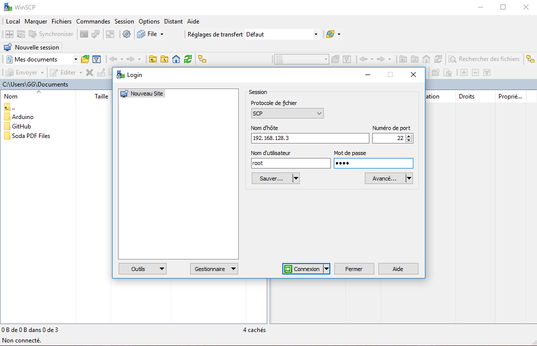
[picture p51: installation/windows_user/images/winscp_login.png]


* On left side of WinSCP you have folders of your computer and on the right you have the ones of the RedPitaya. Go to /tmp/ folder of the RedPitaya:  
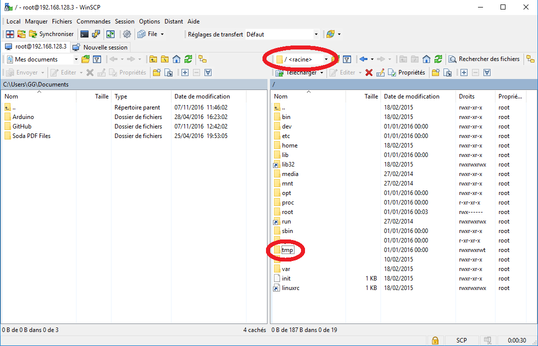
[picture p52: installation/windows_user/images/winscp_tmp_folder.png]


* On the left side select /PRJ-medtec_kit/electronic/modules/software/CFG-aquarium_kit/redpitaya.Then send default_probe to the RedPitaya:  
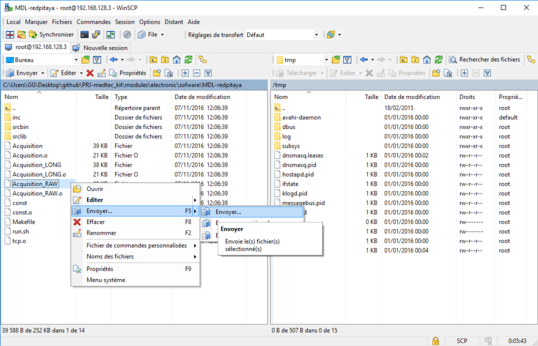
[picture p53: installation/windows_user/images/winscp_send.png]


* Now open putty and connect it to the RedPitaya:  
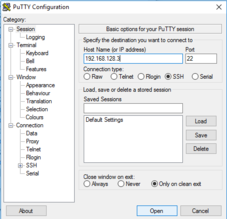
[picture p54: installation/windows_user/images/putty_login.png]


* Then launch the script, you might have to tune the right permission for the file. So in the putty terminal type:  
 `cd /tmp/`  
 `chmod 777 Acquisition_RAW`  
 `./default_probe`

* At this step, the kit is still not power up (if you power it up, you will hear the motor whistle, turn if off). Launch the code on the Redpitaya (enter ./probe or ./default_probe on you terminal) and when it write 'buffer length = 1689' kill it by pressing CTRL+C. Now you can power up the kit (the motor will not whistle like this). We recommand to proceed like this because if not the motor may consume a lot of power and have a short-circuit behavior.

* Launch once again the code (by entering ./default_probe on your terminal). The motor will turn till it comes on the mechanical stop at knock on it (don't worry it's normal). Then it will turn in the other side to reach the beginning of the sweeping zone and make the sweeping movement.

* The default settings are:
    * beginning of measurement 80 mm,
    * end of measurement 160 mm,
    * sampling rate 15.625 Msps,
    * angle of the sector 60°,
    * speed of the motor 3 tour per second,
    * amplification command at beginning of measurement 0.1 V (0.3 dB of amplification),
    * amplification at end of measurement 1 V (43.5 dB of amplification).

* When you want to stop press CTRL+C, to quit the ssh connection just enter exit in your terminal.

## Display

We have not develope a soft to display the image on windows yet, windows users have to use a smartphone with the echopen app.

We do our best to make a simple soft on windows for the processing as soon as possible.

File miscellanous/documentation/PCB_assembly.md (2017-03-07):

name of PCB on the back of the PCB

type of component + footprint
-resistor
-diode (line for cathode)
-condensator electrolitic (white mark for grd (minimum potential))
-tantalium condensator are polarise, line for maximum potential
-condensator ceramic
-transistor (strip draw on PCB)
-MOSFET back draw on PCB
-IC indication of top left (LM555 OPA625...)
-test point (not mandatory)

can solder only the back of the PCB

difficulties to retire solder

connection between two PCB SMA or 02x01 header (choose)

assembly advise chronology:
1) cut an experimenation in half (2 times 19 tracks). Solder 01x19 socket on it (not all, one by one with the daughter boards) first one for power suplly (18V from laboratory supply) and one for the first PCB.
put a reminder of the 19 tracks
2) solder DB-supply_v1, check with oscillo or multimeter for +12V on, -12V on, +5V on, -5V on, 3.3V on (rechercher le numéro des piste correspondant)
led D2 must light on
3) solder DB-motor_control (mettre quelquepart un code arduino qui pulse simplement pour verifer le pulse d'excitation et pulse RP de synchro)
touchy la liaison avec la RedPitaya.
4) solder DB-high_voltage check with oscilloscope (need attenuative /10 probe) or multimeter
5) solder DB-pulser with oscillo trigger on ITF9 with other probe measure pulse output (PX or PY...) don't forget to link DB-high_voltage output (PX or PY) to high voltage input of DB-pulser (PX or PY for sma)
add foto of MAX4940 evaluation kit (for the given version)
6) solder DB-TRswitch except jumper. Link 5) to 6) (sma cable preferably, pX to pY), now put second probe of oscillo on test point 1 (W1) ->oscillo screenshot. If ok, solder jumper (foto?). 
7) now one can plug a transducer to DB-pulse (pX), put it in a mug full of water, changing oscillo setting (around 10us, 100mV) and facing transducer to a "wall" of the mug one can see echoes!!! ouh yeah
8) now one can link AD8331 eval-kit.
9) solder DB-filter, DB-envelop_detection and dB-interface
10) new code in arduino
11) pulg IN1 of RP to px of db-interface, IN2 to py and OUT1 to ad8331 (foto) or pz of db-interface if db-trs_tgc_v2 and RP to motor_control
12) send code in the redpitaya and enjoy

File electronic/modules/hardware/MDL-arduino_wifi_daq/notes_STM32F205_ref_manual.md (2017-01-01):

# Notes on the STM32F205 Reference manual  [](@description Notes on the STM32F205 for quick ADCs)

* [Source PDF : reference Manual](/electronic/modules/hardware/MDL-arduino_wifi_daq/datasheets/en.CD00225773_STM32F2x5_RefManual.pdf).
* [Other interesting : STM32TM’s ADC modes and their applications](/electronic/modules/hardware/MDL-arduino_wifi_daq/datasheets/en.CD00258017.pdf)

* [Inspiration for the code](http://microcontroleurs.blogspot.fr/2015/07/realisation-dune-carte-dacquision-moins.html)

Discussions are taking place to use the max speed on the Feather WICED:

* [See on Adafruit GithubRepo](https://github.com/adafruit/Adafruit_WICED_Arduino/issues/58) 
* [on adafruit forums](https://forums.adafruit.com/viewtopic.php?f=57&p=527280)

## ADC 

* Configurable DMA data storage in Dual/Triple ADC mode
* Configurable delay between conversions in Dual/Triple interleaved mode
* ADC conversion time: 0.5 μs with APB2 at 60 MHz
* ADC supply requirements: 2.4 V to 3.6 V at full speed and down to 1.8 V at slower speed
* ADC input range: V REF– ≤ V IN ≤ V REF+
* DMA request generation during regular channel conversion

### Fast conversion mode

It is possible to perform faster conversion by reducing the ADC resolution. The RES bits are used to select the number of bits available in the data register. The minimum conversion time for each resolution is then as follows: 

* 12 bits: 3 + 12 = 15 ADCCLK cycles
* 10 bits: 3 + 10 = 13 ADCCLK cycles
* 8 bits: 3 + 8 = 11 ADCCLK cycles
* 6 bits: 3 + 6 = 9 ADCCLK cycles

## Calibration

Using the feather WICED to produce a waveform:



### Versions of code so far

* [INO for close to 2Msps, 2ADCs interleaved](/electronic/modules/hardware/MDL-arduino_wifi_daq/feather_tests/2ADC2UDP.ino)

Compared to the waveform detailed above, gives the following acquisition:



### ADC common control register (ADC_CCR)

When the DMA mode is enabled (DMA bit set to 1 in the ADC_CR2 register), after each conversion of a regular channel, a DMA request is generated. This allows the transfer of the converted data from the ADC_DR register to the destination location selected by the software

* MULTI[4:0]: Multi ADC mode selection
* 10001 to 11001: Triple mode: ADC1, 2 and 3 working together
* 10111: interleaved mode only

### Comment on the code

#### Initialization of the ADC

```c
  // We configure the ADC1 and ADC2
  // Setting max sampling rate
  rcc_set_prescaler(RCC_PRESCALER_ADC, RCC_ADCPRE_PCLK_DIV_2);
  adc_set_sample_rate(ADC1, ADC_SMPR_1_5);
  adc_set_sample_rate(ADC2, ADC_SMPR_1_5);
  //  adc_set_sample_rate(ADC2, ADC_SMPR_3);

  //6=0110 for dual regular simultaneous mode
  // FOR STM32F1 -- DUALMOD[3:0]: Dual mode selection is on ADC control register 1 (ADC_CR1) - has to be changed
  // Bits 19:16 DUALMOD[3:0]: Dual mode selection
  // 7 is for interleaved mode.
  ADC1->regs->CR1 |= 7 << 16;

  //only one input in the sequence for both ADC: the channel 1

  adc_set_reg_seqlen(ADC1, 1);
  adc_set_reg_seqlen(ADC2, 1);
  adc_set_reg_seqlen(ADC3, 1);
  // Aiming at Interleaved mode on 1 channel in continuous conversion mode: triple ADC mode
  //channel 1 (PA1) on ADC1
  ADC1->regs->SQR1 |= 0;
  ADC1->regs->SQR2 = 0;
  ADC1->regs->SQR3 = 1; //00000.00000.00001
  //channel 1 (PA1) on ADC2
  ADC2->regs->SQR1 |= 0;
  ADC2->regs->SQR2 = 0; //00000.00000.00000
  ADC2->regs->SQR3 = 1; //00000.00000.00010
  //channel 1 (PA1) on ADC3
  ADC3->regs->SQR1 |= 0;
  ADC3->regs->SQR2 = 0; //00000.00000.00000
  ADC3->regs->SQR3 = 1; //00000.00000.00010
```

#### Acquisition

Acquisition takes place in a loop, where 2*BUFFERSIZE data is acquired. Values from ADC1 and ADC2 go into val1 and val2.

```c
    while (i < BUFFERSIZE) {
      // ADC : page 212 to 254 in the reference manual

      //start conversion
      ADC1->regs->CR2 |= ADC_CR2_SWSTART;
      ADC2->regs->CR2 |= ADC_CR2_SWSTART;

      // Wait the end of the conversion
      while (!(ADC1->regs->SR & ADC_SR_EOC)) ;
      while (!(ADC2->regs->SR & ADC_SR_EOC)) ;

      // Get the values converted from the two ADCs.
      // They are sharing the same channel, in interleaved mode
      val1[i] = (int16)(ADC1->regs->DR & ADC_DR_DATA);
      val2[i] = (int16)(ADC2->regs->DR & ADC_DR_DATA);
      i++;
   }
```

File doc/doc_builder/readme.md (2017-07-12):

# Application

## Name
[`APP-doc_builder`]()

## Title
Documentation builder application

## About
Small command line application that parses all echOpen repositories to find documentation
elements. This application produce static HTML web sites for different documentation
levels.

## Installation
* Python 3.6.0 for Windows 64bits (install for all users)
* `python -m pip install --upgrade pip` (from superuser console)
* `pip install markdown` (from superuser console)
* `pip install PyYAML` (from superuser console)
* `pip install lxml` (from superuser console)
  * if it doesn't work go on http://www.lfd.uci.edu/~gohlke/pythonlibs/#lxml and download to src/vendor `lxml‑3.6.4‑cp35‑cp35m‑win32.whl` or `lxml‑3.6.4‑cp35‑cp35m‑win_amd64.whl` depending on your Python platform. Then run :
  * `pip install vendor/lxml-3.6.4-cp35-cp35m-win32.whl` (from superuser console)
  * `pip install vendor/lxml-3.6.4-cp35-cp35m-win_amd64.whl` (from superuser console)

## Run

To rebuild documentation as a new static web site :

1. Run a console
2. Change directory to PRJ-medtec_kit/doc/doc_builder
3. Remove all files in PRJ-medtec_kit/doc/www
4. Execute python script doc_builder.py
5. Copy newly created static web site from PRJ-medtec_kit/doc/www/slot1 to echOpen production web serveur under documentation http://echopen.org/doc-website/

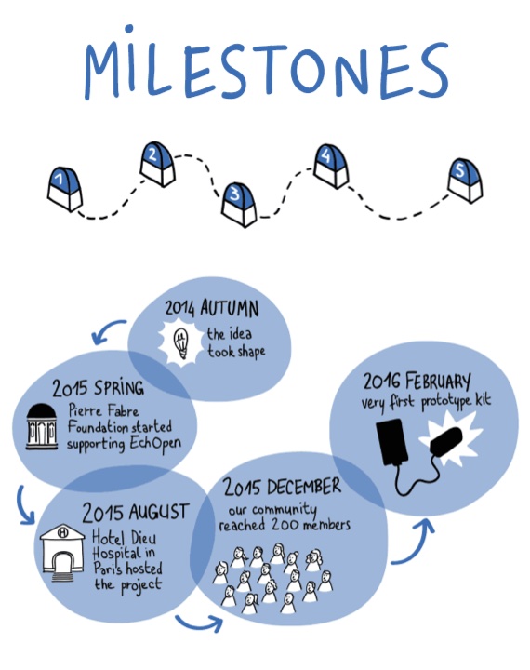
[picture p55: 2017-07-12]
doc/doc_builder/src/default_www/images/about/1.jpg

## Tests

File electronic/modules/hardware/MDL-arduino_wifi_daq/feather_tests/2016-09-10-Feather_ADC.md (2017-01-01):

# Playing with the STM32F205 (Feather WICED ADC)

## First tests

Code can be found [here](/electronic/modules/hardware/MDL-arduino_wifi_daq/feather_tests/ReadPins.ino).

Testing it with a 10kHz (0-1V) sine gives the following

and with  a 10kHz (0-1V) sine:

Not satisfactory.

## Digging into the low-level code

Code can be found [here](/electronic/modules/hardware/MDL-arduino_wifi_daq/feather_tests/Registers.ino).

### Sources

* http://microcontroleurs.blogspot.fr/2015_07_01_archive.html?view=sidebar interessant!

 RCC_ADCPRE_PCLK_DIV_2 can replace ADC_PRE_PCLK2_DIV_2 .. or so it seems

### Question

Question is found on [github](https://github.com/adafruit/Adafruit_WICED_Arduino/issues/58):

I'm trying to see how fast the Feather WICED ADC can go. I've been trying with ` analogRead()`, and at first sight, I'm getting data at around 50ksps. Will be posting the raw data later on to support this.

Now, I've begun digging into the maple ADC and corresponding code, and I've put together a piece of [code to test acquisition speed](https://gist.github.com/kelu124/ee02b6f98d8997404783aa3043d40c1e). This code compiles nicely, but doesn't work (nothing on serial). I'm unsure of the reason behind this, and I guess some registers need to be finetuned.

For example, the enumeration for STM32F1 differs from STM32F2, as said by [leaflab](https://github.com/leaflabs/leaflabs-docs/blob/master/source/libmaple/overview.rst). However, using `ADC_SMPR_1_5` during compilation works, but not the actual `ADC_SMPR_3`.

Working on this at the moment, but would appreciate if you had some ideas on what I could do next, I'll be updating/documenting the issue in the same time.

### Playing with the same code (D+1)

But removing all references to the second ADC (and so .. to the third as well), the [code works](/electronic/modules/hardware/MDL-arduino_wifi_daq/feather_tests/Registers1Msps.ino).

Interfacing the feather to a i2c 128x64 oled display, I can see that it takes around 990 us to get 1000 samples. That's a bit more than 1Msps - and it should be enough to get a signal coming from the emulator.

Moreover, with this working, we can see that the input signal coming from 0 to 3.3V gives 0 to 4095.. as expected. Since the output of [Goblin](/electronic/modules/hardware/MDL-analog_processing_ic/) is up to 3.3V, it means I can connect goblin's output to this one, and try to trig on the same trigger as the emulator as well. Will need a level shifter.

### Playing with the same code (D+2)

Been putting the trig on the 5V trigger from the pulser. Works better.

Also doing some averaging.. need to check if it really works.

Anyhow, the [code works](/electronic/modules/hardware/MDL-arduino_wifi_daq/feather_tests/Registers1MspsDisplayTrigged.ino). 

It seems like for 2048 points buffer, only 4 full periods of the pulser are present. This pulser working at 300us intervals, this would put the 
acquisition at 1.7Msps. Need to check what is really the speed of this acquisition.

Seeing echoes as well from a real transducer =)

## Being a bit more serious

The code is here [ADC2UDP-Cleaning.ino](/electronic/modules/hardware/MDL-arduino_wifi_daq/feather_tests/ADC2UDP-Cleaning.ino).

### Testing the speed of acquisition
 
I got 24x128 points (data is [here](/electronic/modules/hardware/MDL-arduino_wifi_daq/data/128x24points.data), decimated 128 times: and I see 22.2 decimated points for a period of 300us. 

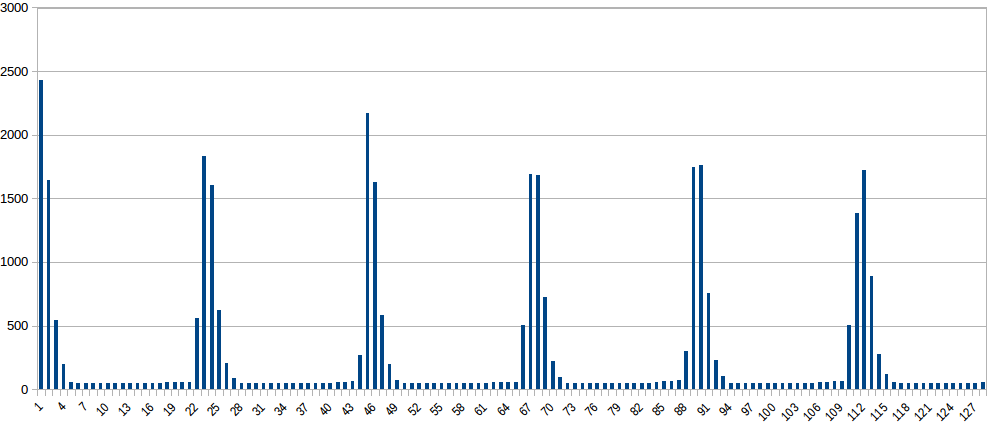
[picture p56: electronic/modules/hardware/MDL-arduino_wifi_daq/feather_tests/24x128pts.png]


Thats 533 points per period. Since it's a 300us period, the overall acquisition speed is close to 1.776Msps at 12 bits, using only one ADC.

### Getting an image with [Silent](/silent/) and Goblin

#### Background

Silent is the emulating module, which emulates a ultrasound piezo. It's output before Goblin, the analog processing module, is as follows:



and after



#### Acquisition

The data was acquired with [Croaker](/electronic/modules/hardware/MDL-arduino_wifi_daq/) through the UDP streaming option. Lines are 128 points long (hence 72us long), and the value is coded over 12 bits, from 0-4095, corresponding to 0-3.3V. [Data is here](/croaker)

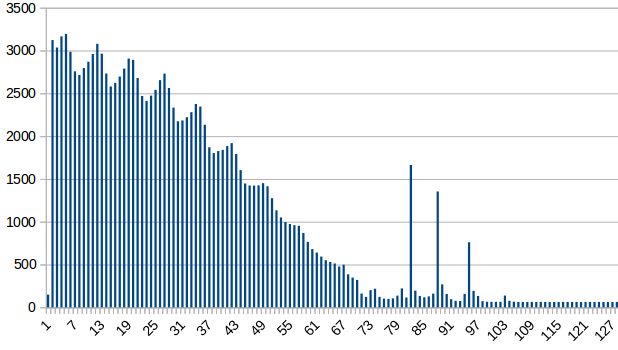
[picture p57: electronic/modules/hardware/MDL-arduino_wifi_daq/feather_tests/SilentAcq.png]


Comparing with the source signal, it seems that we are late on acquisition: the trigger took some time.

Peaks on the 3 smaller peaks afterwards are on points 82, 88 and 95. That's 6.5 points on average between each, or 3.66 us between each peak. In the config of Silent, we see that each is separated by roughly 7 us. That would mean the ADC speed varies. Needs to be explored.

#### Next steps: getting more juice from the ADCs

* http://www.stm32duino.com/viewtopic.php?t=757&start=10
* Datasheets..

New acquisition is as follows:

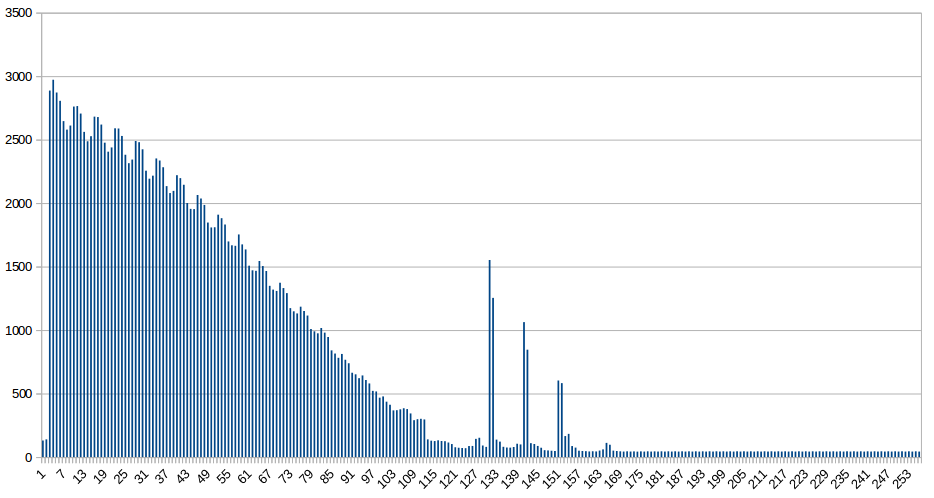
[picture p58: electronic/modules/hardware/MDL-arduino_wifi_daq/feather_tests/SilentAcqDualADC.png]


The peaks get better resolved. [Data is here](/electronic/modules/hardware/MDL-arduino_wifi_daq/data/dualADC.data) -and [Arduino code is here](/electronic/modules/hardware/MDL-arduino_wifi_daq/feather_tests/2ADC2UDP.ino). Roughly doubling the sampling rate.

* Video of the setup, showing the OLED screen showcasing the signal : https://www.youtube.com/watch?v=iyfDMsgAquI

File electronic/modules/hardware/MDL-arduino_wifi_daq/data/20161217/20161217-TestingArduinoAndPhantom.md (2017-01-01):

# 2016-12-17 -- Lab Log

## Aim of the work

* **Test the (lower-speed) acquisition using an arduino's ADC (~2Msps), which also streams over wifi, over UDP.**
* **Build and test a very basic, yet accurate, phantom**

## Setup

The classical one. Using the [pulser](/electronic/modules/hardware/MDL-pulser_ic/) module, [analog processing](/electronic/modules/hardware/MDL-analog_processing_ic/) module, and a [arduino-like](/croaker) to capture and stream the data. Piezo moved by a servo ([module](/electronic/modules/hardware/MDL-piezoservo/)).

### Setup:

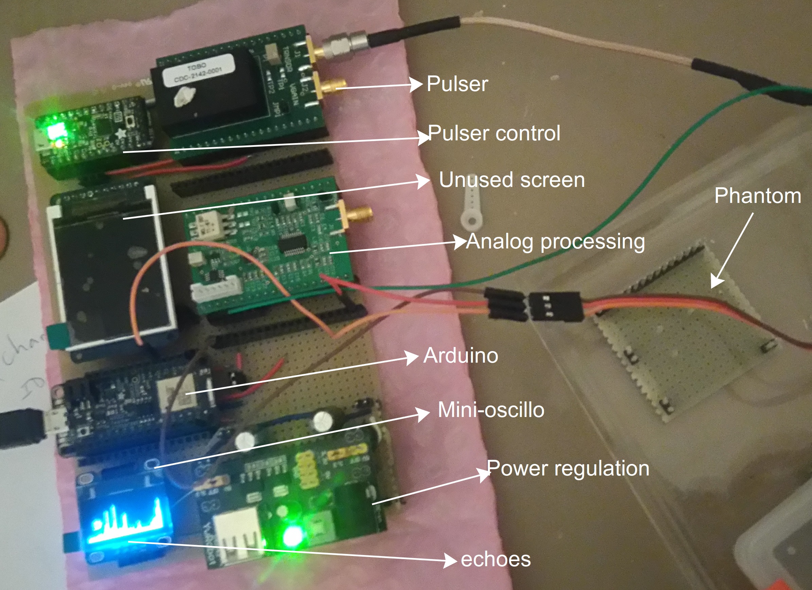
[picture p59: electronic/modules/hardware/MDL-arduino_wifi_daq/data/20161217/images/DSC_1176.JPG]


### Phantom

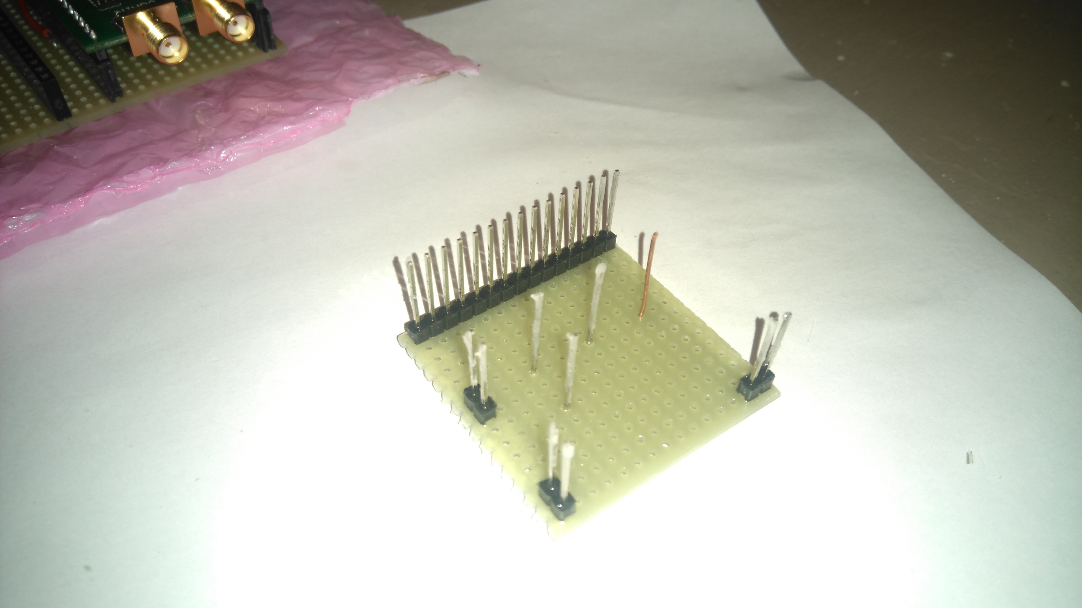
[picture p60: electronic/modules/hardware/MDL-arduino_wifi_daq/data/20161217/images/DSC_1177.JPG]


## Capturing data

Script used were:

* `nc -lu 5005 > 20161217-222737.data` -- to acquire the [raw data](/electronic/modules/hardware/MDL-arduino_wifi_daq/data/20161217/raw_data/20161217-222737.data) streamed by the arduino on port 5005
* `python CreateCSV2.py 20161217-222737.data` -- using the [CreateCSV2](/electronic/modules/hardware/MDL-arduino_wifi_daq/data/manual/CreateCSV2.py) script to generate proper data using the good format from the raw data file. This was later consolidated in a single image.

## Raw images

### Acquisition of 4 images

Presented non scan converted

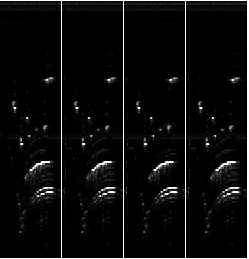
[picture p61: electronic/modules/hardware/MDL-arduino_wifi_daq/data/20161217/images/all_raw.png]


### Comparison of raw images to the phantom

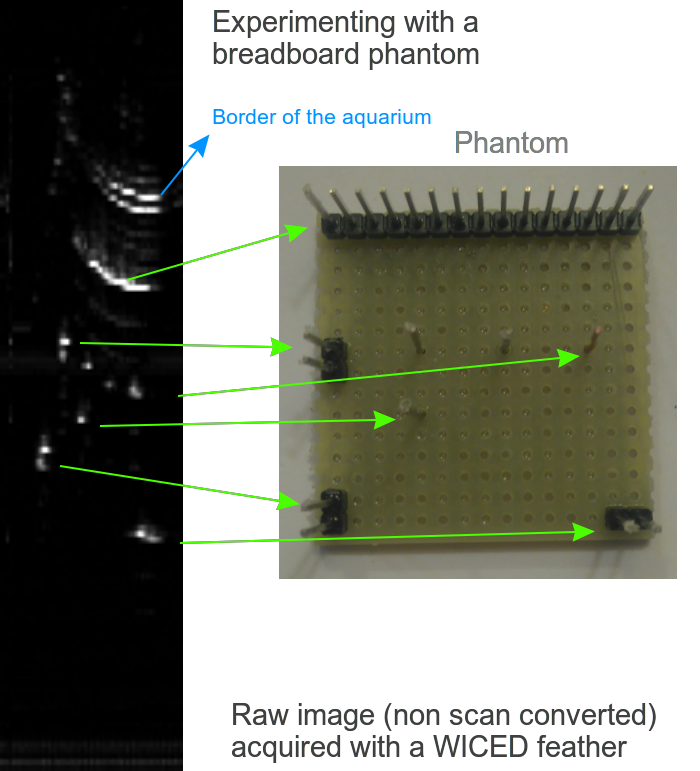
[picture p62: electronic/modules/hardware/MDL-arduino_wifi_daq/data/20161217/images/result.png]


## Preparing the image

I aggregated the 4 images in one image with the [rebuild script](/electronic/modules/hardware/MDL-arduino_wifi_daq/data/20161217/raw_data/rebuild.py) which yielded

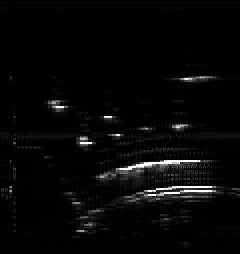
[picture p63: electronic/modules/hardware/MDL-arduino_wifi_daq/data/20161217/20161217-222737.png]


and scan converted it:

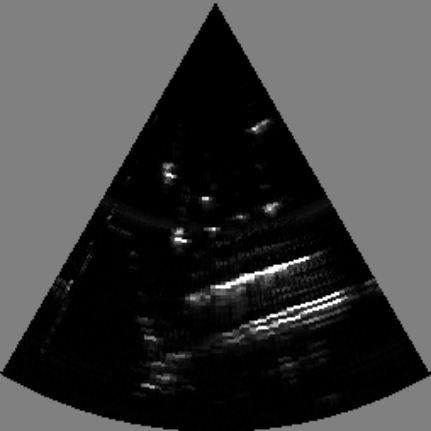
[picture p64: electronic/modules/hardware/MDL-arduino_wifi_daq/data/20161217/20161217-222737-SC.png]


## Conclusion

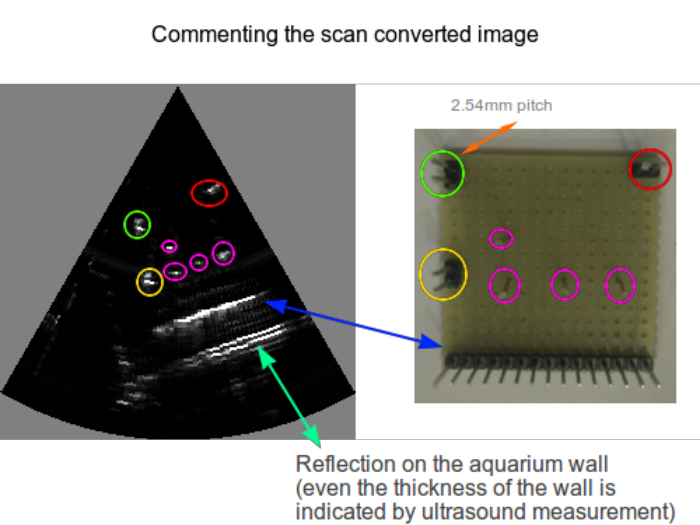
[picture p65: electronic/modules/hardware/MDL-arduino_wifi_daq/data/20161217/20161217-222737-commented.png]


* The acquisition is not too bad, even using an arduino
* The servo may be the limiting element in terms of lateral resolution
    * the breadboard pitch is 0.1 inch, 2.54mm. We resolve this.
* There is an issue with repetition echoes: it may be worth waiting more than 300us between shooting lines.

## Next steps

* Using a gyro
* Using a RPi0 to connect to the [analog processing](/electronic/modules/hardware/MDL-analog_processing_ic/) onboard ADC.

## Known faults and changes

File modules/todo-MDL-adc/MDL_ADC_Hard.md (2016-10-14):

Module: MDL_ADC_Hard

Function: signal processing

Sub-Function: pixel calculation

The response of the transducer is analogical, in order to process it with a microcontroler we need to convert them on the digital form

Input/Output:

Input: analogical signal

Output: digital signal

Solutions: 

version: V1.0

date: 15/04/2016

technology: commercial board (RedPitaya)

Source:

NA

Scheme:

The RedPitaya board as 125MHz ADC: http://wiki.redpitaya.com/index.php?title=Main_Page.

Input/Output: 

Input: analogical signal

Output: digital signal

Pros/Cons/Constraint: 

Pros: relatively easy to use

Cons: expensive board

Constraint: need 5V, 2A power supply

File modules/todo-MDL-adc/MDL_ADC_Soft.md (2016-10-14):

Module: MDL_ADC_Soft

Function: signal processing

Sub-Function: pixel calculation

The response of the transducer is analogical, in order to process it with a microcontroler we need to convert them on the digital form

Input/Output:

Input: analogical signal

Output: digital signal

Solutions: 

version: V1.0

date: 15/04/2016

technology: commercial board (RedPitaya)

Source:

[https://github.com/echopen/Prototype_software/blob/master/V1/RedPitaya/srcbin/Acquisition_RAW.c](https://github.com/echopen/Prototype_software/blob/master/V1/RedPitaya/srcbin/Acquisition_RAW.c)

An API will be made soon.

Flowchart:

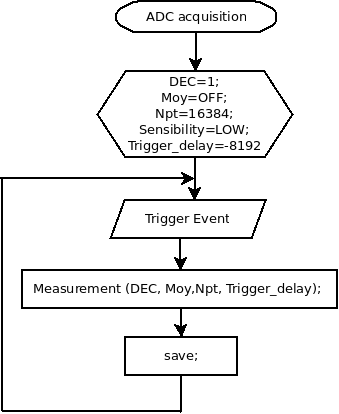
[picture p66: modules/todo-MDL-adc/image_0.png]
image alt text


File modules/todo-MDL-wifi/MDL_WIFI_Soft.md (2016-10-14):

**Module:** data server

**Function:** signal processing

**Sub-Function: **pixel calculating

When the echoes measured by the transducer are converted into digital signal, we have to calculate the pixels and send them to client (smartphone, tablet…).

**Input/Output:**

Input: digital echoes

Output: 8 bits pixel matrix (256 grey levels image)

**Solutions:** 

version: V1.0

date: 02/05/2016

technology: commercial board (RedPitaya) + wifi dongle

**Scheme:**

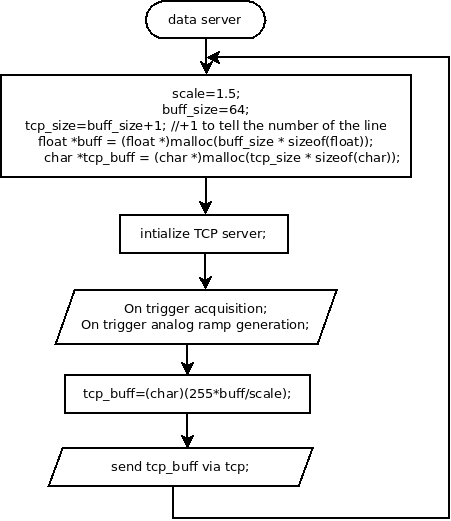
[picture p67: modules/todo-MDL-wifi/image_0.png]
image alt text


**Input/Output: **

Input: digital echoes

Output: digital image send *via *wifi with a TCP protocol

**Pros/Cons/Constraint:** 

Pros: easy to use

Cons: price

Constraint: 5V, 2A power supply

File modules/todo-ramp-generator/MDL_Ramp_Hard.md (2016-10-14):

**Module:** MDL_Ramp_Hard

**Function:** signal processing

**Sub-Function: **amplifying

The amplification factor of the TGC is command by an analogical signal. So we need a DAC in order to generate this analogical signal.

**Input/Output:**

Input: NA

Output: analogic ramp

**Solutions:** 

version: V1.0

date: 02/05/2016

technology: commercial board (RedPitaya)

**Scheme:**

The RedPitaya board as 125MHz DAC: [http://wiki.redpitaya.com/index.php?title=Main_Page](http://wiki.redpitaya.com/index.php?title=Main_Page)

**Input/Output: **

Input: logic (3.3V) pulse (for synchronisation)

Output: analogic ramp for 0 to 1V

**Pros/Cons/Constraint:**

Pros: easy to use

Cons: price

Constraint: 5V 2A power supply

version: V2.0

date: 07/2016

technology: commercial board (RedPitaya)

author: Joris

**Source:**

[https://github.com/echopen/electronic/tree/master/kicad/Modules/MDL_Ramp/MDL_Ramp_V2](https://github.com/echopen/electronic/tree/master/kicad/Modules/MDL_Ramp/MDL_Ramp_V2)

**Scheme:**

The pin connection is given to be implemented with an STM32F401 but can be done for any ucontroler:

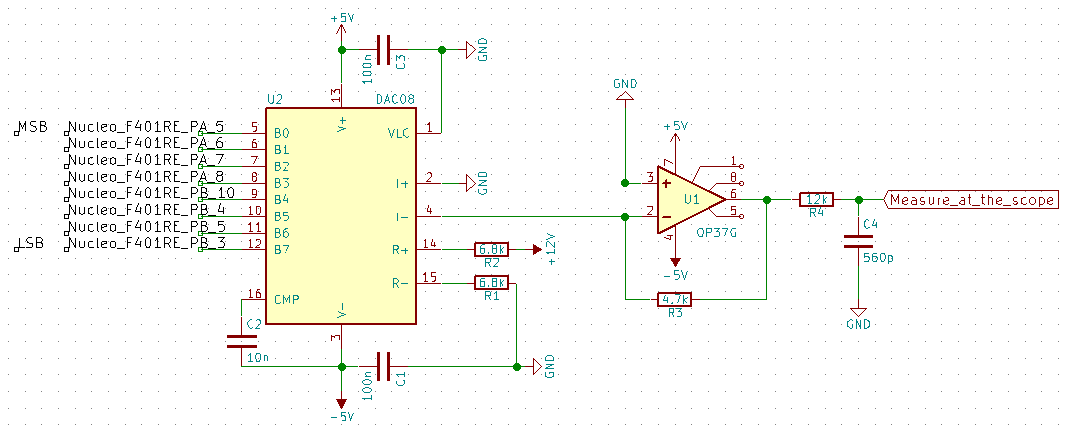
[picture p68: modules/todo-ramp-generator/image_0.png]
image alt text


**BOM:**

<table>
  <tr>
    <td>Reference</td>
    <td>Value</td>
    <td>Library</td>
    <td>Library Ref</td>
  </tr>
  <tr>
    <td>U2</td>
    <td>DAC0800</td>
    <td>adc-dac</td>
    <td>DAC0800</td>
  </tr>
  <tr>
    <td>R2</td>
    <td>6.8k</td>
    <td>device</td>
    <td>R</td>
  </tr>
  <tr>
    <td>R1</td>
    <td>6.8k</td>
    <td>device</td>
    <td>R</td>
  </tr>
  <tr>
    <td>C1</td>
    <td>100n</td>
    <td>device</td>
    <td>C</td>
  </tr>
  <tr>
    <td>C2</td>
    <td>10n</td>
    <td>device</td>
    <td>C</td>
  </tr>
  <tr>
    <td>C3</td>
    <td>100n</td>
    <td>device</td>
    <td>C</td>
  </tr>
  <tr>
    <td>R3</td>
    <td>4.7k</td>
    <td>device</td>
    <td>R</td>
  </tr>
  <tr>
    <td>U1</td>
    <td>OP37G</td>
    <td>linear</td>
    <td>CA3130</td>
  </tr>
  <tr>
    <td>R4</td>
    <td>12k</td>
    <td>device</td>
    <td>R</td>
  </tr>
  <tr>
    <td>C4</td>
    <td>560p</td>
    <td>device</td>
    <td>C</td>
  </tr>
</table>

**Input/Output: **

Input: 8 digital signals

Output: analogic 

**Pros/Cons/Constraint:**

Pros: easy to use

Cons: NA

Constraint: +/- 5V and 12V supply

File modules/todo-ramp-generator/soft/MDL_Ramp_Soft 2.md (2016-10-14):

**Module:** MDL_Ramp

**Function:** signal processing

**Sub-Function: **amplifying

The amplification factor of the TGC is command by an analogical signal. So we need a DAC in order to generate this analogical signal.

**Solutions:** 

version: V1

date: 02/05/2016

author: Jérôme

hardware concerned: MDL_Ramp_V1

**Source:**

[https://github.com/echopen/Prototype_software/blob/master/V1/RedPitaya/srcbin/Acquisition_RAW.c](https://github.com/echopen/Prototype_software/blob/master/V1/RedPitaya/srcbin/Acquisition_RAW.c)

An API will be made soon.

**Solutions:** 

version: V2

date: 07/2016

author: Joris

hardware concerned: MDL_Ramp_V1

**Source:**

[https://github.com/echopen/Prototype_software/blob/master/STM32F4/Ramp_generator/main.cpp](https://github.com/echopen/Prototype_software/blob/master/STM32F4/Ramp_generator/main.cpp)

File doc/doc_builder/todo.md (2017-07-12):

# Project tasks

## Todo

- [ ] TSK-002 : Afficher la page à partir de la transformation Markdown de son contenu
      raw_content et non de la reconstruction de l'index
- [ ] TSK-003 : Les templates des catégories qui sont inclus dans des codes_fence ne sont pas
      affichés comme tels en html
- [ ] TSK-004 : Passer toutes les fichiers de def des catégories dans le même format que
      CAT-report.md (code_fence, block Yaml...)
- [ ] TSK-005 : Récupérer tous les reports de réunions
- [ ] TSK-006 : Faire des scripts de génération de doc depuis serveur Web
- [ ] TSK-007 : Ajouter un viewme.png par défaut pour chaque catégorie

## Done

- [x] TSK-001 : Ajouter le traitement des blocs de meta données sous forme de
      données YAML.

------------------------------------------------------------

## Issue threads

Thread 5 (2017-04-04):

### ISSUE TITLE
remake scheme for motor_control

### ISSUE THREAD

**Issue by Aurelie-Mutschler** [echopen/PRJ-medtec_kit#5]
add cut to -5V track

**Comment by Aurelie-Mutschler** [comment]
former schemes : 
![bottom_view](https://cloud.githubusercontent.com/assets/10047375/24558672/42e7354c-163c-11e7-98c4-5acc43f0fb5e.png)
![front_view](https://cloud.githubusercontent.com/assets/10047375/24558673/42ebe48e-163c-11e7-8083-2d41776d209f.png)
![rp_bottom](https://cloud.githubusercontent.com/assets/10047375/24558674/42ec8be6-163c-11e7-80ef-3f202aa97658.png)
![rrp_front](https://cloud.githubusercontent.com/assets/10047375/24558675/42f0ac44-163c-11e7-895e-7c851c1fb282.png)

**Comment by jerome2echopen** [comment]
redone

**Comment by jerome2echopen** [comment]
I forgot to put the images...
![front_view](https://cloud.githubusercontent.com/assets/14290878/24698332/8b5f7a2a-19f0-11e7-8df2-66274d59180d.png)
![back_view](https://cloud.githubusercontent.com/assets/14290878/24698343/92af07a0-19f0-11e7-9b0e-07fc31a14aa0.png)
![rp_bottom_view](https://cloud.githubusercontent.com/assets/14290878/24698388/bb24f3f2-19f0-11e7-844a-1b8a3e703623.png)
![rp_top_view](https://cloud.githubusercontent.com/assets/14290878/24698393/bfdee54c-19f0-11e7-84ff-95a6990ee574.png)

**Comment by jerome2echopen** [comment]
Update for coherence with daughter board documentation:
![top_view](https://cloud.githubusercontent.com/assets/14290878/25046889/298912b6-2134-11e7-9873-95297eab5d8c.png)
![bottom_view](https://cloud.githubusercontent.com/assets/14290878/25046892/2de3c9dc-2134-11e7-8f32-78ba8e9adea6.png)

cf.: PRJ-medtec_kit/electronic/daughter_boards/DB-motor_control/DB-motor_control_v3/readme.md

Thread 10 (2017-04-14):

### ISSUE TITLE
Complete description of mechanical part in the production guide

### ISSUE THREAD

**Issue by GG23800** [echopen/PRJ-medtec_kit#10]

**Comment by jerome2echopen** [comment]
To complete the kit, one have to 3D print some pieces locate on PRJ-medtec_kit/mecanic/modules. At least we need MDL-motor_support, MDL-rod_fixation and MDL-transducer_support, with these modules we have the stricilly minimum device to make measurement in an acquarium. Use the .stl files present in the different folders for 3d printing them. Note that for the moment MDL-transducer_support will have to be adapted for your own transducer because we have not « serial » transducers to ship with our kit yet. One can do that by using freecad (open the .igs file) modify and then export in .stl file (mesh formats files).

First print MDL-motor_support, at the end it will look to something like that:

![support_raw](https://cloud.githubusercontent.com/assets/14290878/25046759/8b27c11c-2133-11e7-9142-a07238787caa.JPG)

![support_raw2](https://cloud.githubusercontent.com/assets/14290878/25046762/93c5875a-2133-11e7-88be-5a98856cd623.JPG)

Take off the plastique support, there is still plastic in the hole where we will put the motor :

![support_raw3_2](https://cloud.githubusercontent.com/assets/14290878/25046774/a1f4587e-2133-11e7-84dc-2f13306aca71.JPG)

Take it off too with pliers for example, and it’s finish:

![support_evide](https://cloud.githubusercontent.com/assets/14290878/25046778/ab14e1f8-2133-11e7-951e-f97ca449919f.JPG)

Now fix the motor to this support with 2 or 4 screw 3 mm diameter, 6mm long.

Now print MDL-rod-fixation, the two holes on each side of this part of the cylinder. The bigger one is for the motor axe. Fix this axis with a 3mm diameter 10 mm long screw. This screw must be 10 mm minimum cause it must stick out so it will hit the motor_support when initialising (searching it's 0). The second one is used to fix the rod, prefer using wood screw 3 mm diameter.

![montage1](https://cloud.githubusercontent.com/assets/14290878/25046818/cf8b07e2-2133-11e7-9160-16d13f03c956.JPG)

The rod is a metal rod 4 mm diameter, prefer stainless steel, because it will be immersed in water, We use 100 mm long rod, but only limitation on the length is that the transducer must be immersed and the electrical connection of the transducer must not.

Then print the tranducer support and fix it to the rod.

![finish](https://cloud.githubusercontent.com/assets/14290878/25046827/dc7a2442-2133-11e7-823f-2ffeb7d1adaa.JPG)

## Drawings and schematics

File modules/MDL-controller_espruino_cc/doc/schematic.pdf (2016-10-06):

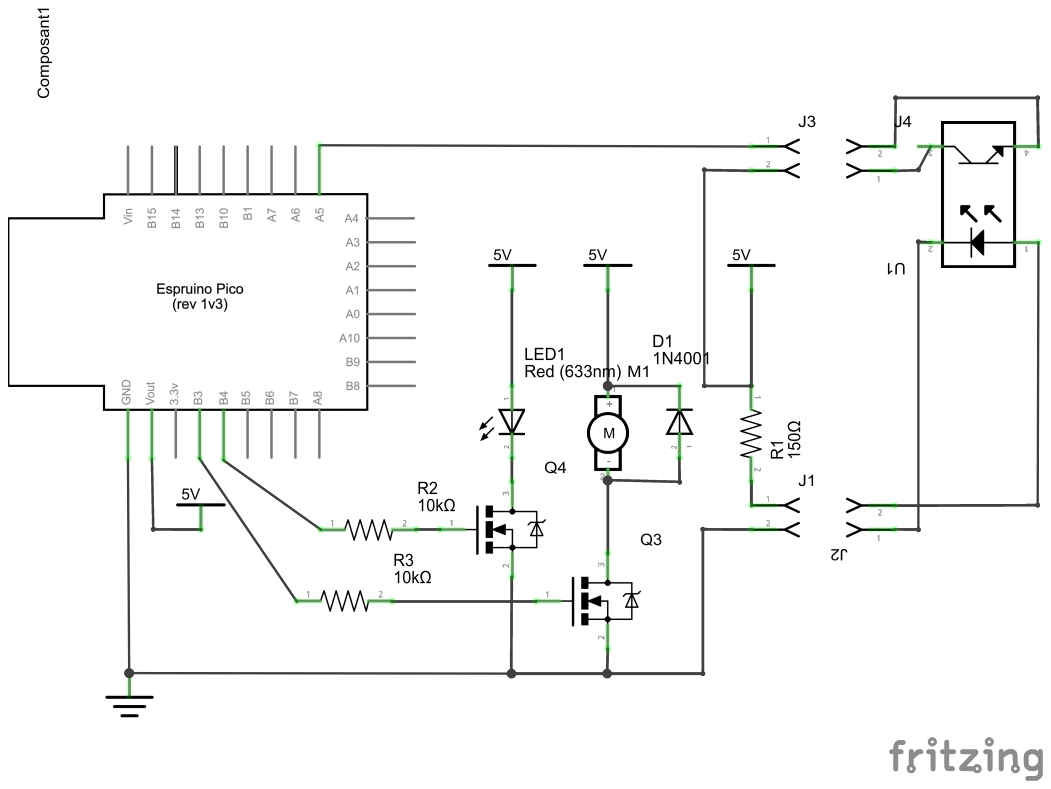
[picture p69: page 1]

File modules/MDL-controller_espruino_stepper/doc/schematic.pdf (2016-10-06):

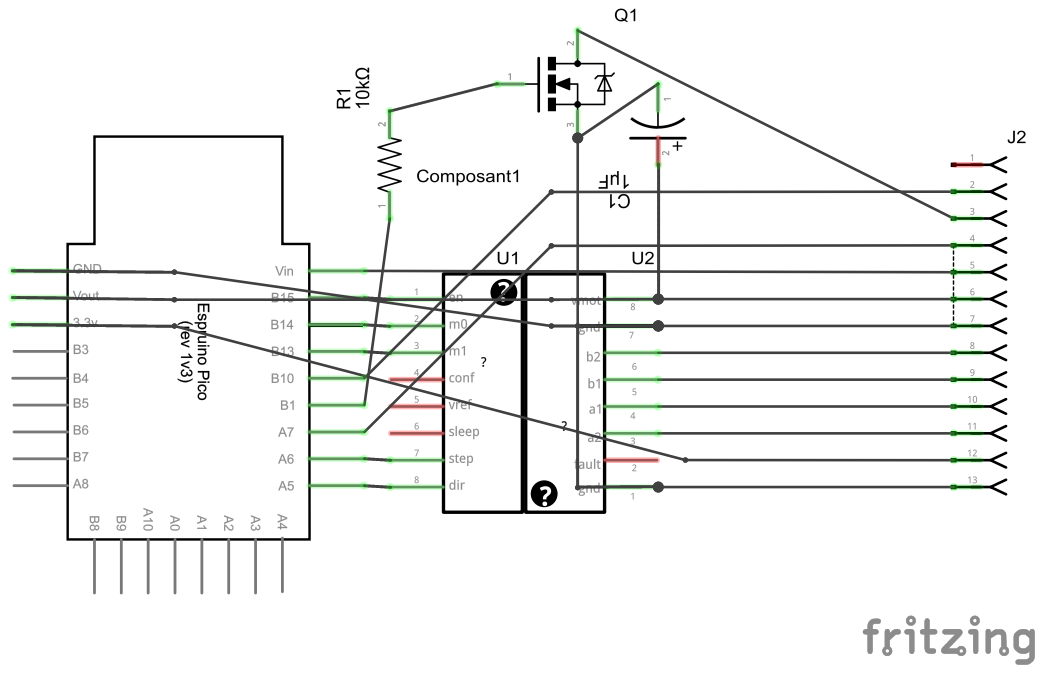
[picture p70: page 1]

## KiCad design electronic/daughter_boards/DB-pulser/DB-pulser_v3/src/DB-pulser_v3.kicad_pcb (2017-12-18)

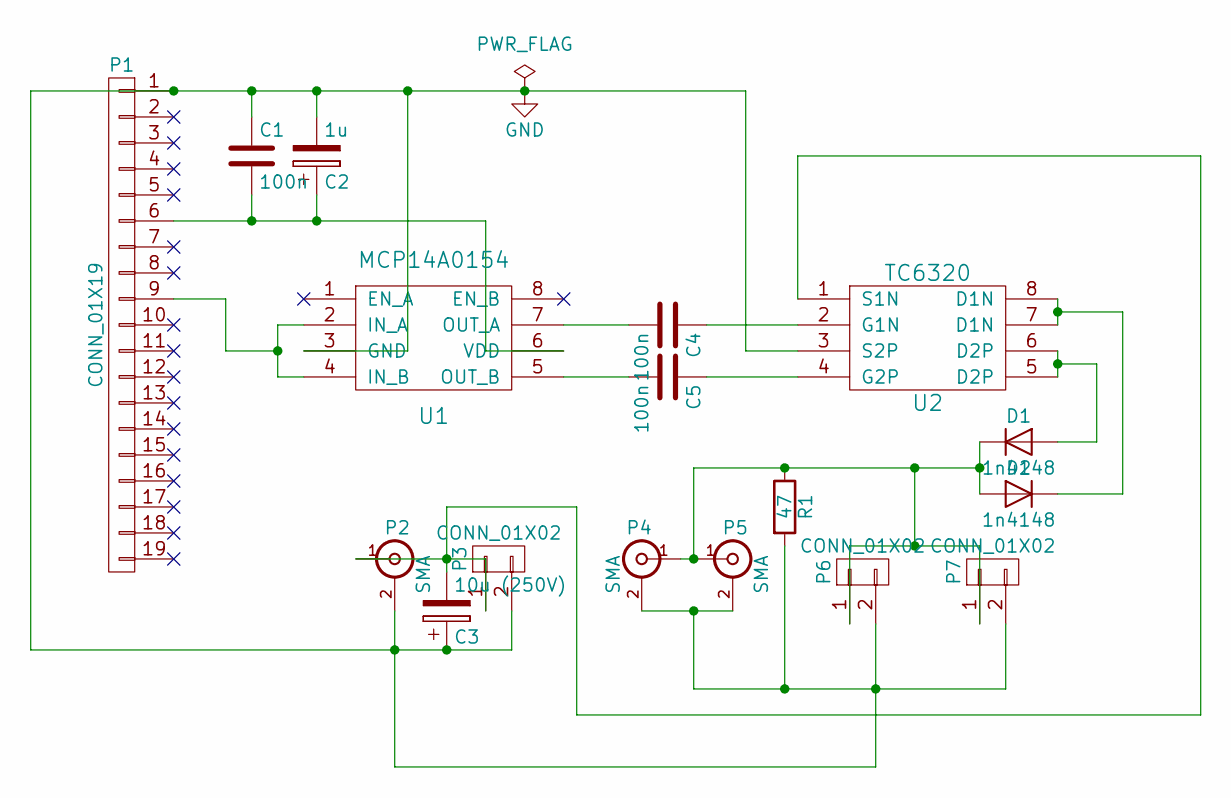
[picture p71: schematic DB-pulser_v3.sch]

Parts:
C1, C4, C5: 100n; C_small_TH_echopen
C2: 1u; CP_small_TH_echopen
C3: 10u (250V); CP_small_TH_echopen
D1, D2: 1n4148; D_TH_common
P1: CONN_01X19; Header_pin_angled_1x19
P2, P4, P5: SMA
P3, P6, P7: CONN_01X02; Socket_1x02
R1: 47; Resistor_TH_common
U1: MCP14A0154; MSOP-8
U2: TC6320; SOIC-8

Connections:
GND: C1.1, C2.2, C3.1, P1.1, P2.2 (Ext), P3.2, P4.2 (Ext), P5.2 (Ext), P6.2, P7.2, R1.2, U1.3 (GND), U2.3 (S2P)
unnamed: C1.2, C2.1, P1.6, U1.6 (VDD)
unnamed: C3.2, P2.1 (In), P3.1, U2.1 (S1N)
unnamed: C4.1, U2.2 (G1N)
unnamed: C4.2, U1.7 (OUT_A)
unnamed: C5.1, U2.4 (G2P)
unnamed: C5.2, U1.5 (OUT_B)
unnamed: D1.1 (K), D2.2 (A), P4.1 (In), P5.1 (In), P6.1, P7.1, R1.1
unnamed: D1.2 (A), U2.5 (D2P), U2.6 (D2P)
unnamed: D2.1 (K), U2.7 (D1N), U2.8 (D1N)
unnamed: P1.9, U1.2 (IN_A), U1.4 (IN_B)

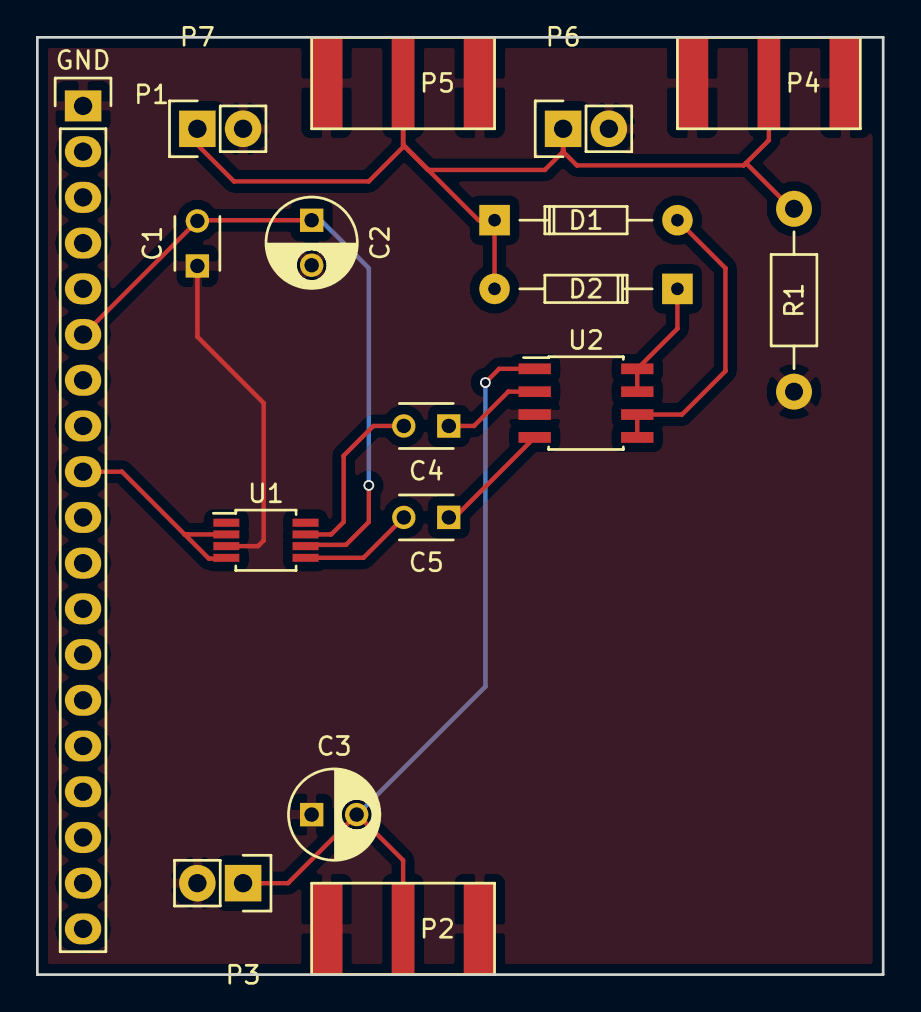
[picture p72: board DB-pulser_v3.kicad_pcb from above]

Board: 2 copper layers, 47.0 x 52.1 mm, 17 parts (0 on the bottom side), 11 nets.

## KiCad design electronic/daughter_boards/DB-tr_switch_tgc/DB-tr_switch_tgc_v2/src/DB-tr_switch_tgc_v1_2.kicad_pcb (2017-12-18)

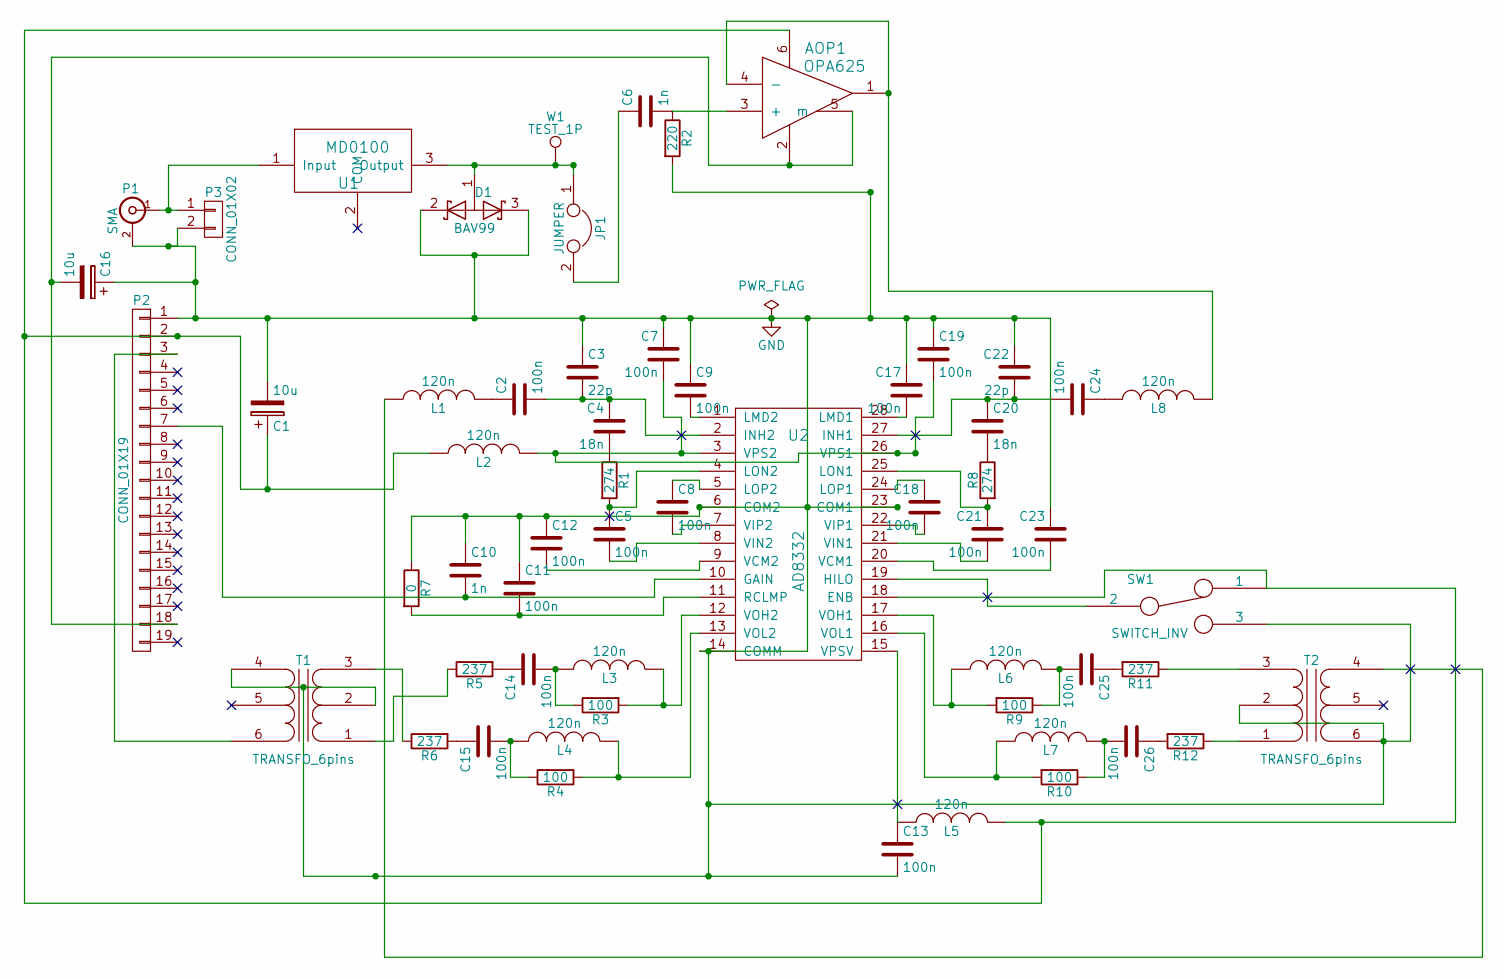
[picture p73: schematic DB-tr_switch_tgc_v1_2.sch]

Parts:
AOP1: OPA625; SOT-23-6_Handsoldering(OPA625)
C1, C16: 10u; CMS_1206
C2, C5, C7, C8, C9, C11, C12, C13, C14, C15, C17, C18, C19, C21, C23, C24, C25, C26: 100n; CMS_0603
C3, C22: 22p; CMS_0603
C4, C20: 18n; CMS_1206
C6, C10: 1n; CMS_0603
D1: BAV99; SOT-23
JP1: JUMPER; Jumper
L1, L2, L3, L4, L5, L6, L7, L8: 120n; CMS_0603
P1: SMA
P2: CONN_01X19; Header_pin_angled_1x19
P3: CONN_01X02; Socket_Strip_Angled_1x02
R1, R8: 274; CMS_0603
R2: 220; CMS_0603
R3, R4, R9, R10: 100; CMS_0603
R5, R6, R11, R12: 237; CMS_0603
R7: 0; Resistor_TH_common
SW1: SWITCH_INV; SW_Micro_SPST
T1, T2: TRANSFO_6pins; Transfo_6pins(coilcraft)
U1: MD0100; SOT89-3_(MD0100)
U2: AD8332; TSSOP-28(AD8332)
W1: TEST_1P; Test_Point_Keystone_5000-5004_Miniature

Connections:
GND: C1.2, C3.1, C7.1, C9.1, C10.1, C11.1, C12.1, C13.2, C16.1, C17.1, C19.1, C22.1, C23.1, D1.2 (K), D1.3 (K), P1.2 (Ext), P2.1, P3.2, R2.2, R7.1, SW1.3, T1.2 (PM), T1.4 (S2), T2.2 (PM), T2.6 (S1), U2.6 (COM2), U2.14 (COMM), U2.23 (COM1)
unnamed: AOP1.1, AOP1.4 (-), L8.1
unnamed: AOP1.2, AOP1.5 (m), C16.2, P2.18
unnamed: AOP1.3 (+), C6.2, R2.1
unnamed: AOP1.6, C1.1, L2.1, L5.2, P2.2, SW1.1, U2.18 (ENB)
unnamed: C2.1, L1.2
unnamed: C2.2, C3.2, C4.1, U2.2 (INH2)
unnamed: C4.2, R1.1
unnamed: C5.1, R1.2, U2.4 (LON2)
unnamed: C5.2, U2.8 (VIN2)
unnamed: C6.1, JP1.2
unnamed: C8.1, U2.5 (LOP2)
unnamed: C8.2, U2.7 (VIP2)
unnamed: C9.2, U2.1 (LMD2)
unnamed: C10.2, P2.7, U2.10 (GAIN)
unnamed: C11.2, R7.2, U2.11 (RCLMP)
unnamed: C12.2, U2.9 (VCM2)
unnamed: C13.1, L5.1, U2.15 (VPSV)
unnamed: C14.1, R5.2
unnamed: C14.2, L3.2, R3.1
unnamed: C15.1, R6.2
unnamed: C15.2, L4.2, R4.1
unnamed: C17.2, U2.28 (LMD1)
unnamed: C18.1, U2.24 (LOP1)
unnamed: C18.2, U2.22 (VIP1)
unnamed: C7.2, C19.2, L2.2, U2.3 (VPS2), U2.26 (VPS1)
unnamed: C20.1, C22.2, C24.2, U2.27 (INH1)
unnamed: C20.2, R8.1
unnamed: C21.1, R8.2, U2.25 (LON1)
unnamed: C21.2, U2.21 (VIN1)
unnamed: C23.2, U2.20 (VCM1)
unnamed: C24.1, L8.2
unnamed: C25.1, R11.2
unnamed: C25.2, L6.2, R9.1
unnamed: C26.1, R12.2
unnamed: C26.2, L7.2, R10.1
unnamed: D1.1 (A), JP1.1, U1.3 (Output), W1.1
unnamed: L1.1, T2.4 (S2)
unnamed: L3.1, R3.2, U2.12 (VOH2)
unnamed: L4.1, R4.2, U2.13 (VOL2)
unnamed: L6.1, R9.2, U2.17 (VOH1)
unnamed: L7.1, R10.2, U2.16 (VOL1)
unnamed: P1.1 (In), P3.1, U1.1 (Input)
unnamed: P2.3, T1.6 (S1)
unnamed: R5.1, T1.1 (PR2)
unnamed: R6.1, T1.3 (PR1)
unnamed: R11.1, T2.3 (PR1)
unnamed: R12.1, T2.1 (PR2)
unnamed: SW1.2, U2.19 (HILO)

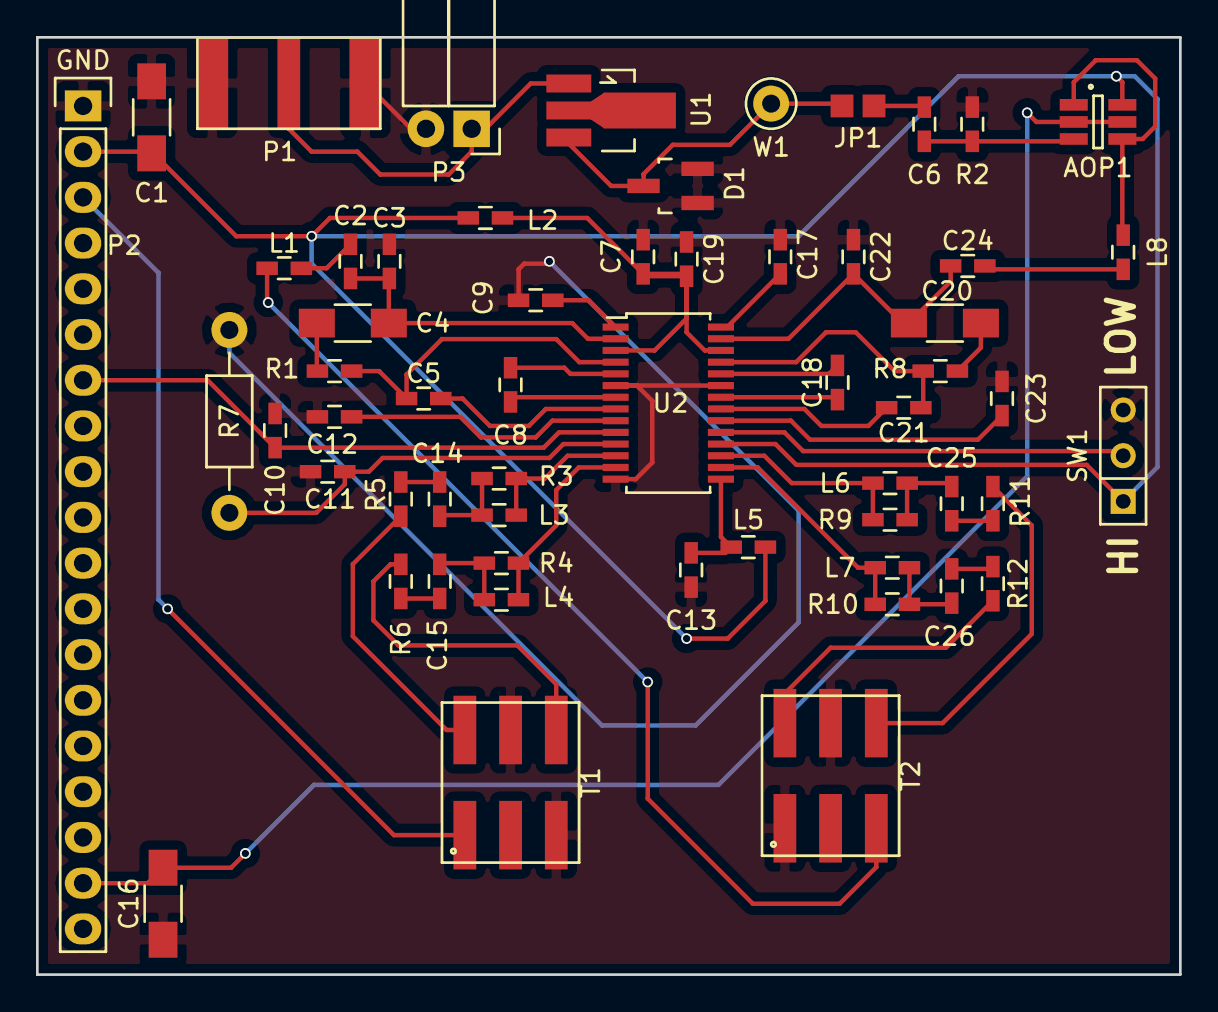
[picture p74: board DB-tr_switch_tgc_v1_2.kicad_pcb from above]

Board: 2 copper layers, 63.5 x 52.1 mm, 58 parts (0 on the bottom side), 49 nets.

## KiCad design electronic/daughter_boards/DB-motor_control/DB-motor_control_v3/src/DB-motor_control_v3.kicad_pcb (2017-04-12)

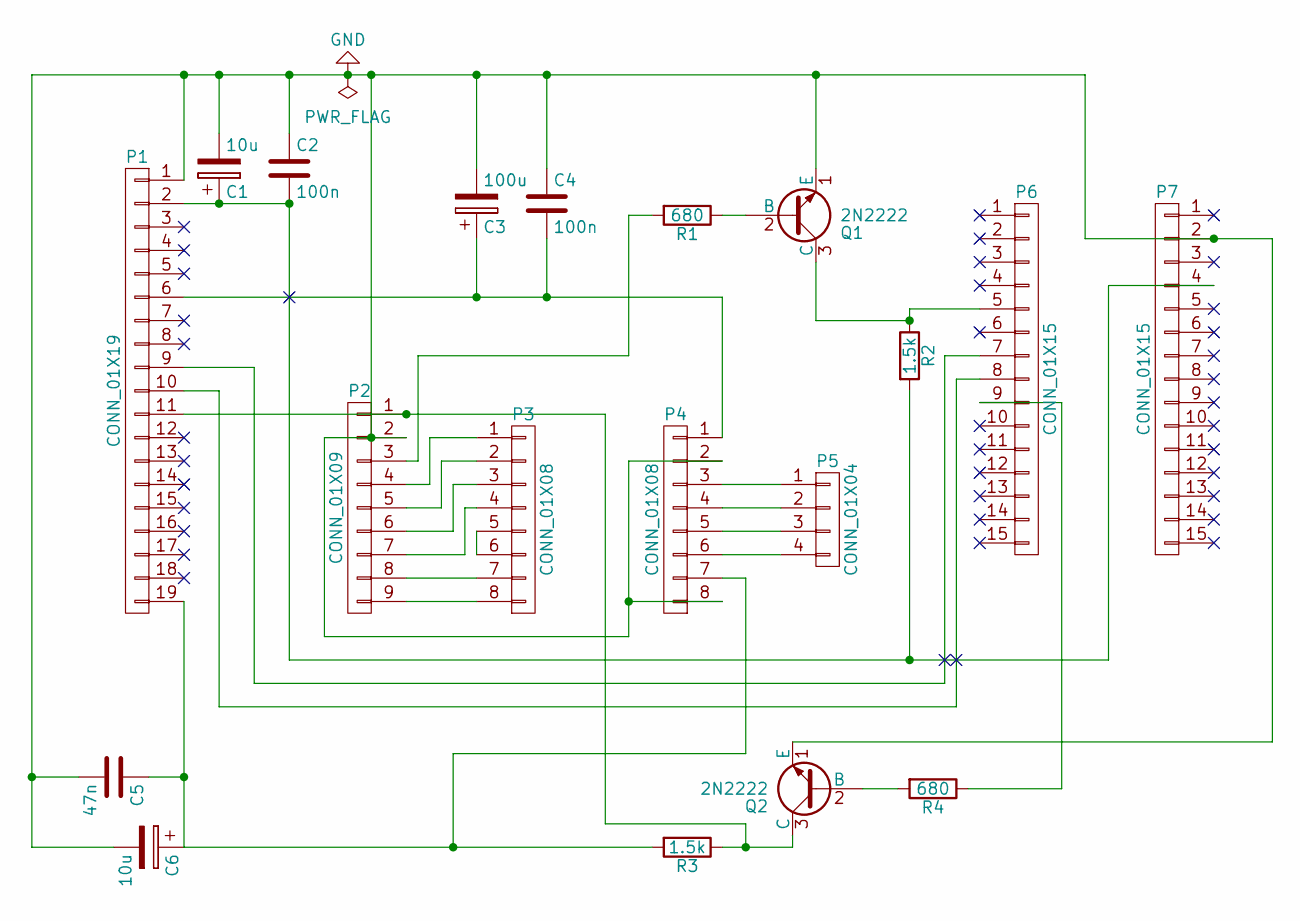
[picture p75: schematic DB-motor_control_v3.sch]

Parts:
C1, C6: 10u; CP_small_TH_echopen
C2, C4: 100n; C_small_TH_echopen
C3: 100u; CP_small_TH_echopen
C5: 47n; C_small_TH_echopen
P1: CONN_01X19; Header_pin_angled_1x19
P2: CONN_01X09; Socket_1x09
P3, P4: CONN_01X08; Pin_Header_Straight_1x08
P5: CONN_01X04; Pin_Header_Straight_1x04
P6, P7: CONN_01X15; Pin_Header_Straight_1x15
Q1, Q2: 2N2222; TO-18_TH_common
R1, R4: 680; Resistor_TH_common
R2, R3: 1.5k; Resistor_TH_common

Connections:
GND: C1.2, C2.1, C3.2, C4.1, C5.2, C6.2, P1.1, P2.2, P4.2, P4.8, P7.2, Q1.1 (E), Q2.1 (E)
unnamed: C1.1, C2.2, P1.2, P7.4, R2.2
unnamed: C3.1, C4.2, P1.6, P4.1
unnamed: C5.1, C6.1, P1.19, P4.7, R3.2
unnamed: P1.9, P6.7
unnamed: P1.10, P6.8
unnamed: P1.11, P2.1, Q2.3 (C), R3.1
unnamed: P2.3, R1.2
unnamed: P2.4, P3.1
unnamed: P2.5, P3.2
unnamed: P2.6, P3.3
unnamed: P2.7, P3.4
unnamed: P2.8, P3.7
unnamed: P2.9, P3.8
unnamed: P3.5, P3.6
unnamed: P4.3, P5.1
unnamed: P4.4, P5.2
unnamed: P4.5, P5.3
unnamed: P4.6, P5.4
unnamed: P6.5, Q1.3 (C), R2.1
unnamed: P6.9, R4.1
unnamed: Q1.2 (B), R1.1
unnamed: Q2.2 (B), R4.2

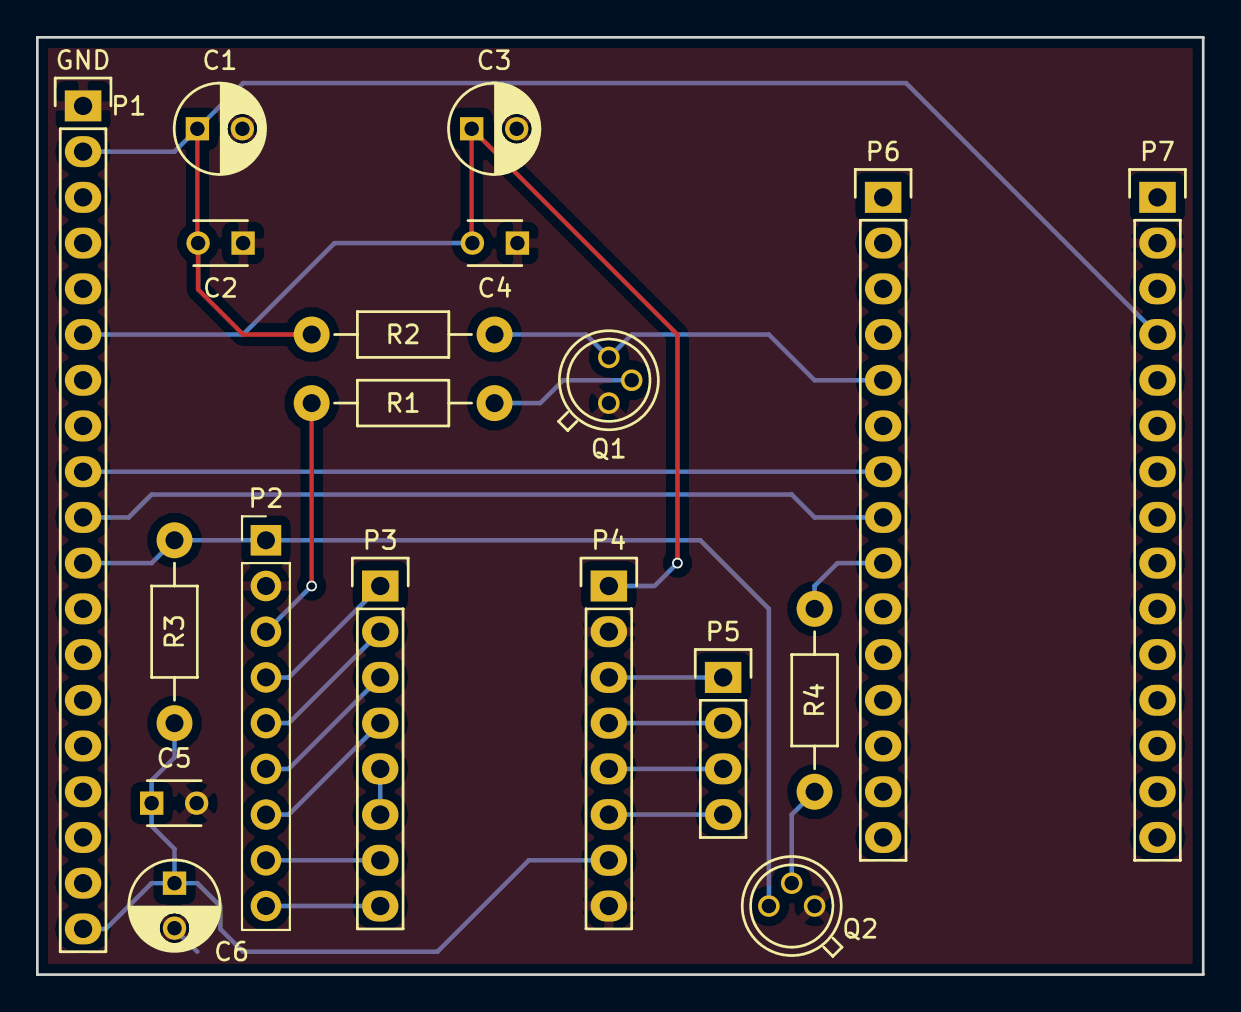
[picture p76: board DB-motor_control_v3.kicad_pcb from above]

Board: 2 copper layers, 64.8 x 52.1 mm, 19 parts (0 on the bottom side), 23 nets.

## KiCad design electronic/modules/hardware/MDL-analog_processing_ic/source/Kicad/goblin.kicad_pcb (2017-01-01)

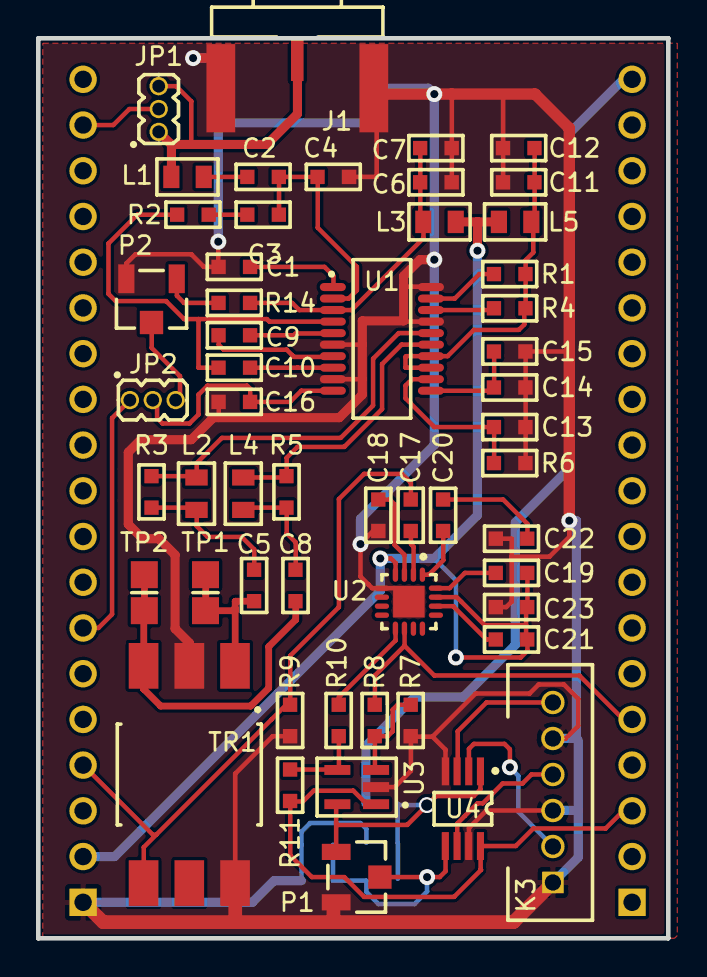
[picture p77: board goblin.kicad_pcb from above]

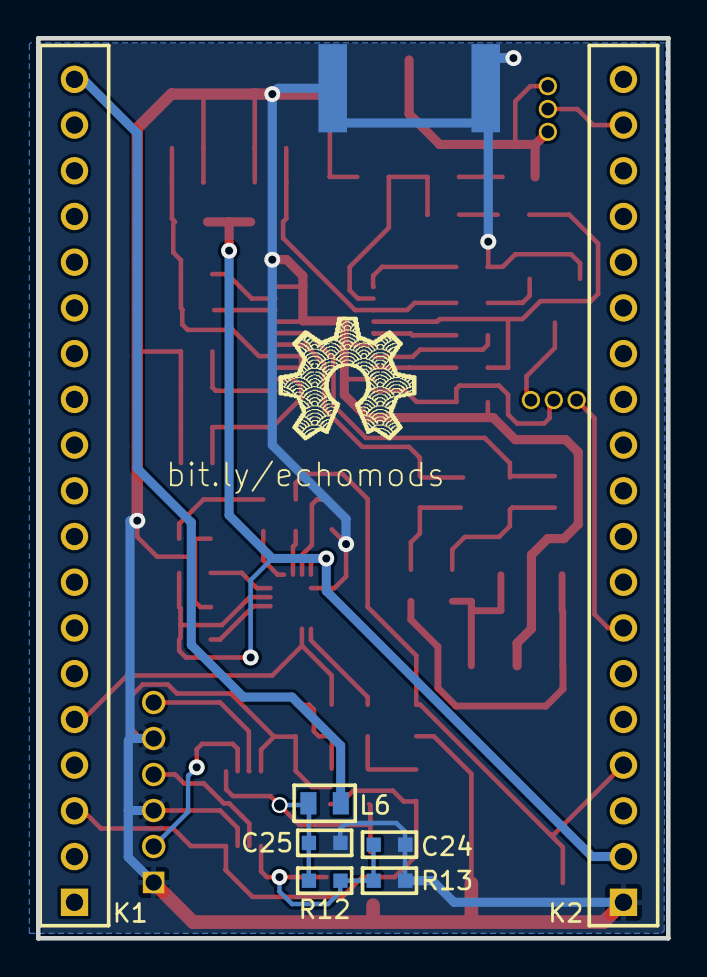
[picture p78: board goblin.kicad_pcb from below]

Board: 2 copper layers, 35.0 x 50.0 mm, 60 parts (7 on the bottom side), 46 nets.

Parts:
C1, C2, C3, C4, C5, C6, C7, C8, C9, C10, C11, C12, C13, C14, C15, C16, C17, C18, C19, C20, C21, C22, C23, C24, C25: Capacitor; SM0603_3D_cap
J1: SMA; AMPHENOL_132357-11
Jumper1, Jumper2: Jumper; SULLINS_GRPB031VWVN
K1, K2: Header19; PLS_2.54mm-19
K3: Header6; Molex_89400-061
L1, L2, L3, L4, L5, L6: Inductor; SM_0805_INDUCTANCE_3D
P1, P2: TrimPot; TRIM_BOURNS_3223W
R1, R2, R3, R4, R5, R6, R7, R8, R9, R10, R11, R12, R13, R14: Resistor; SM0603_3D_res
TP1, TP2: TP; NICOMATIC_C12000B
TR1: RF_Transformer_1; XFMR_MINI-CIRCUITS_KK81
U1: AD8331ARQZ; SOP64P600X175-20N
U2: ADL5511ACPZ-R7; QFN50P300X300X80-17N-S175
U3: AD8691; TSOT-5(RT-5)
U4: AD7274; RM-8

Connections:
3.3VA: C25.1, L6.2, P1.1, R12.1, U3.5, U4.1
/ADC: K1.3, R11.1, U3.1, U4.8
/ADC_VREF: C24.1, P1.2, R12.2, R13.1, U4.5
/GAIN: Jumper2.1, K2.7
/VGA_IN: Jumper1.2, K2.18
/VGA_OUT2: C17.2, K2.4, R9.1, TR1.4
/VGA_OUT_N: C5.2, TP1.1, TR1.1
/VGA_OUT_P: C8.2, TP2.1, TR1.3
/V_ENVELOPE: K1.5, R8.2, U2.10
AGND: C1.2, C4.2, C6.2, C7.2, C11.2, C12.2, C13.2, C14.2, C15.2, C16.2, C18.2, C22.2, C23.2, C24.2, C25.2, J1.2, K2.1, K3.1, K3.3, K3.5, P1.3, P2.3, R6.2, R7.1, R9.2, R13.2, TR1.2, TR1.6, U1.6, U1.9, U1.17, U1.20, U2.5, U2.17, U3.2, U4.4, U4.7
unnamed: C1.1, U1.1
unnamed: C2.1, L1.2
unnamed: C2.2, C3.1, C4.1, U1.2
unnamed: C3.2, R2.1
unnamed: C5.1, L2.1, R3.2
unnamed: C6.1, C7.1, L3.2, R14.1, U1.3
unnamed: C8.1, L4.1, R5.2
unnamed: C9.1, U1.5
unnamed: C9.2, U1.7
unnamed: C10.1, R2.2, U1.4
unnamed: C10.2, U1.8
unnamed: C11.1, C12.1, L5.2, R1.2, R4.2, U1.13, U1.14
unnamed: C13.1, R6.1, U1.12
unnamed: C14.1, C15.1, U1.11
unnamed: C16.1, Jumper2.2, U1.10
unnamed: C17.1, U2.2
unnamed: C18.1, U2.3
unnamed: C19.1, U2.16
unnamed: C20.1, U2.1
unnamed: C20.2, C22.1
unnamed: C21.1, U2.14
unnamed: J1.1, Jumper1.1, Jumper1.3, L1.1
unnamed: Jumper2.3, P2.2
unnamed: K3.2, U4.2
unnamed: K3.4, U4.6
unnamed: K3.6, U4.3
unnamed: L2.2, R3.1, U1.16
unnamed: L4.2, R5.1, U1.15
unnamed: P2.1, R14.2
unnamed: R1.1, U1.19
unnamed: R4.1, U1.18
unnamed: R7.2, R8.1, U3.3
unnamed: R10.1, R11.2, U3.4
unnamed: R10.2, U2.9
VDD_3.3V: K1.19, L6.1
VDD_5V: C19.2, C21.2, C23.1, K2.2, L3.1, L5.1, U2.4, U2.15

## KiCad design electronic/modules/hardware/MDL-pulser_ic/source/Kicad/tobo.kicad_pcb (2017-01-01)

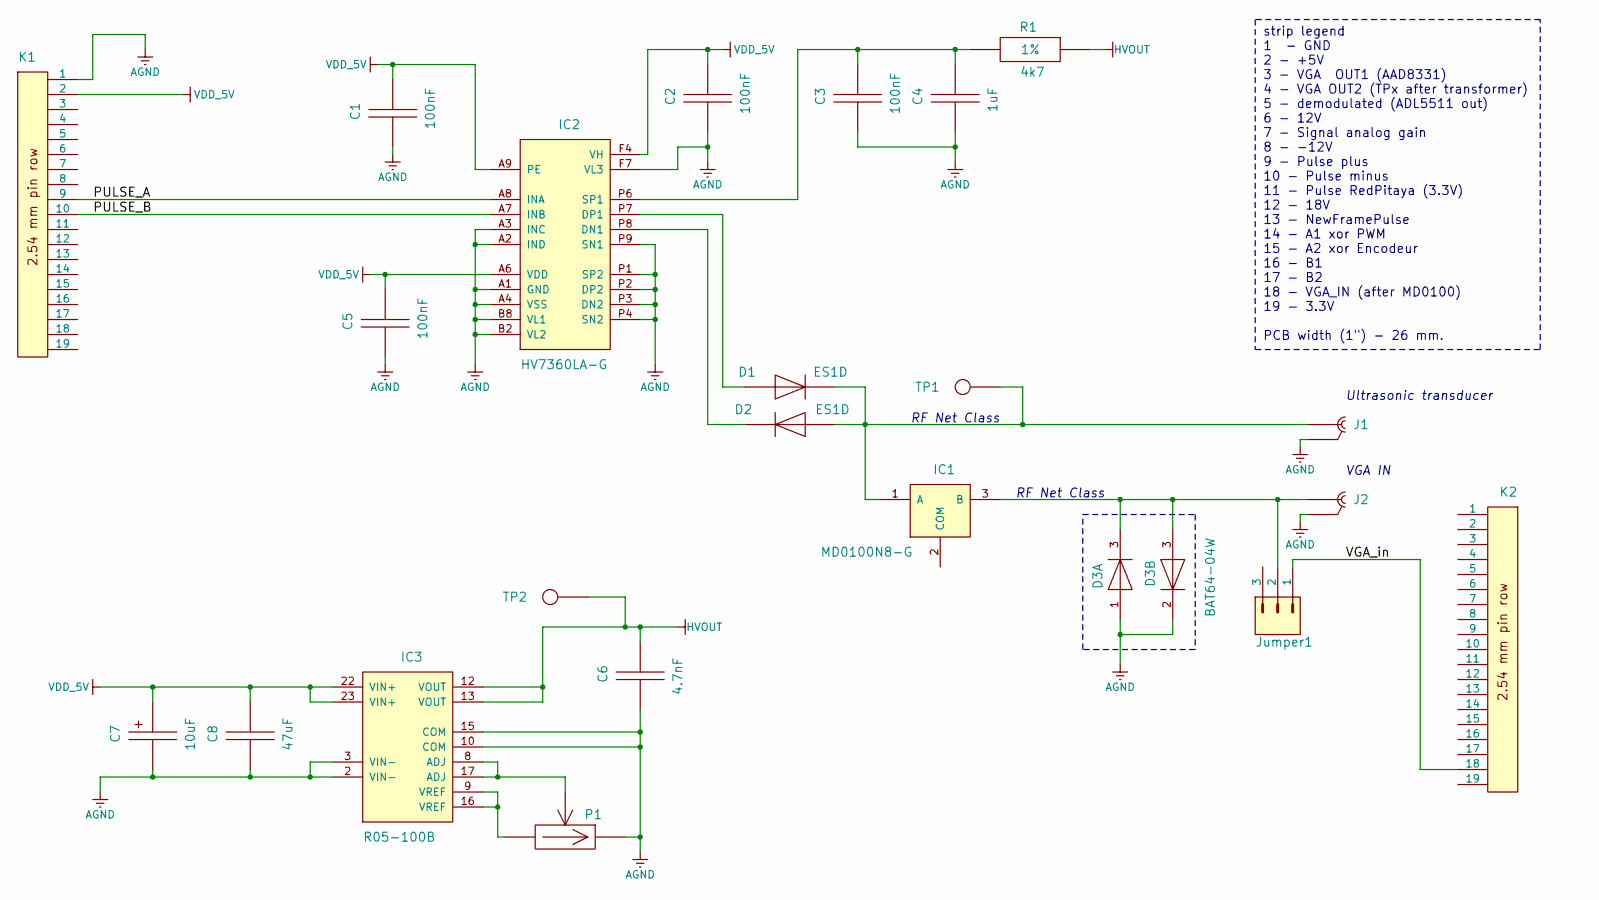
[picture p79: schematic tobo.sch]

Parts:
C1, C2, C3, C5: Capacitor; SM0603_3D_cap
C4: Capacitor; CAPC5650X165N; Tolerance ±10%; Voltage 200V; Manufacturer Part Number CC2220_1UF_200V_10%_X7R
C6: Capacitor; CAPC2012X110N; Tolerance ±10%; Voltage 250V; Manufacturer1 Part Numb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 GRM21AR72E472KW01D
C7: Capacitor_polar; CAPMP3528X210N; Tolerance ±10%; Voltage 16V; Manufacturer Part Number CTE3528-21_10UF_16V_10%_LESR0800
C8: Capacitor; CAPC3216X180N; Tolerance ±20%; Voltage 25V; Manufacturer Part Number C3216X5R1E476M160AC
D1, D2: Diode; DIOM5027X244N; Voltage 200V; Part Description Fast Rectifier
D3: BAT64-04W; SOT65P210X100-3N; Voltage 40V; Part Description Silicon Schottky Double Diode
IC1: MD0100N8-G; SOT89; Part Description Ultra-Sound HV Switch
IC2: HV7360LA-G; BGA22C50P9X14_500X700X105; Part Description High Speed, ±100V 2.5A Two or Three Lev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
IC3: R05-100B; PWS_RECOM_R05-100B; Part Description +5VDC to +55-135VDC 5W Power Supply
J1, J2: SMA; AMPHENOL_132357-11; Part Description SMA End Launch Jack for 1.58mm PCB, 50 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
Jumper1: Jumper; SULLINS_GRPB031VWVN; Part Description 3 Contact 0.5\" Pitch Single-In-Line Ve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
K1, K2: Header19; PLS_2.54mm-19
P1: TrimPot; TRIM_BOURNS_3223W; Tolerance ±20%; Part Description 11 Turns SMD Trimpot® Trimming Potentio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
R1: Resistor; RESC3216X65N; Tolerance_Show 1%; Tolerance ±1%; Part Description General Purpose Thick Film Chip Resistor
TP1, TP2: TP; NICOMATIC_C12000B; Part Description SMD Test Point

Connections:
/PULSE_A: IC2.A8 (INA), K1.9
/PULSE_B: IC2.A7 (INB), K1.10
/VGA_in: Jumper1.1, K2.18
AGND: C1.2, C2.2, C3.2, C4.2, C5.2, C6.2, C7.2, C8.2, D3.1 (COMAC), D3.2 (C), IC2.A1 (GND), IC2.A2 (IND), IC2.A3 (INC), IC2.A4 (VSS), IC2.B2 (VL2), IC2.B8 (VL1), IC2.F7 (VL3), IC2.P1 (SP2), IC2.P2 (DP2), IC2.P3 (DN2), IC2.P4 (SN2), IC2.P9 (SN1), IC3.2 (VIN-), IC3.3 (VIN-), IC3.10 (COM), IC3.15 (COM), J1.2, J2.2, K1.1, P1.3 (CW)
HVOUT: C6.1, IC3.12 (VOUT), IC3.13 (VOUT), R1.1, TP2.1
unnamed: C3.1, C4.1, IC2.P6 (SP1), R1.2
unnamed: D1.1 (C), D2.2 (A), IC1.1 (A), J1.1, TP1.1
unnamed: D1.2 (A), IC2.P7 (DP1)
unnamed: D2.1 (C), IC2.P8 (DN1)
unnamed: D3.3 (C), IC1.3 (B), J2.1, Jumper1.2
unnamed: IC3.9 (VREF), IC3.16 (VREF), P1.1 (CCW)
unnamed: IC3.8 (ADJ), IC3.17 (ADJ), P1.2 (W)
VDD_5V: C1.1, C2.1, C5.1, C7.1, C8.1, IC2.A6 (VDD), IC2.A9 (PE), IC2.F4 (VH), IC3.22 (VIN+), IC3.23 (VIN+), K1.2

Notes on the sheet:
strip legend 1 - GND 2 - +5V 3 - VGA OUT1 (AAD8331) 4 - VGA OUT2 (TPx after transformer) 5 - demodulated (ADL5511 out) 6 - 12V 7 - Signal analog gain 8 - -12V 9 - Pulse plus 10 - Pulse minus 11 - Pulse RedPitaya (3.3V) 12 - 18V 13 - NewFramePulse 14 - A1 xor PWM 15 - A2 xor Encodeur 16 - B1 17 - B2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
RF Net Class
VGA IN
Ultrasonic transducer

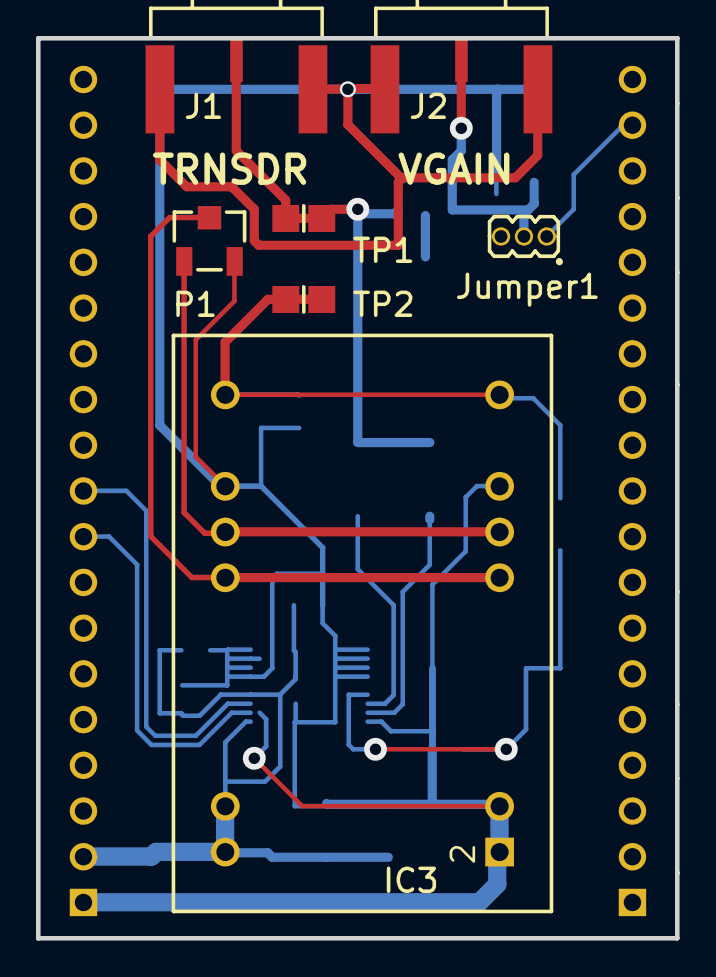
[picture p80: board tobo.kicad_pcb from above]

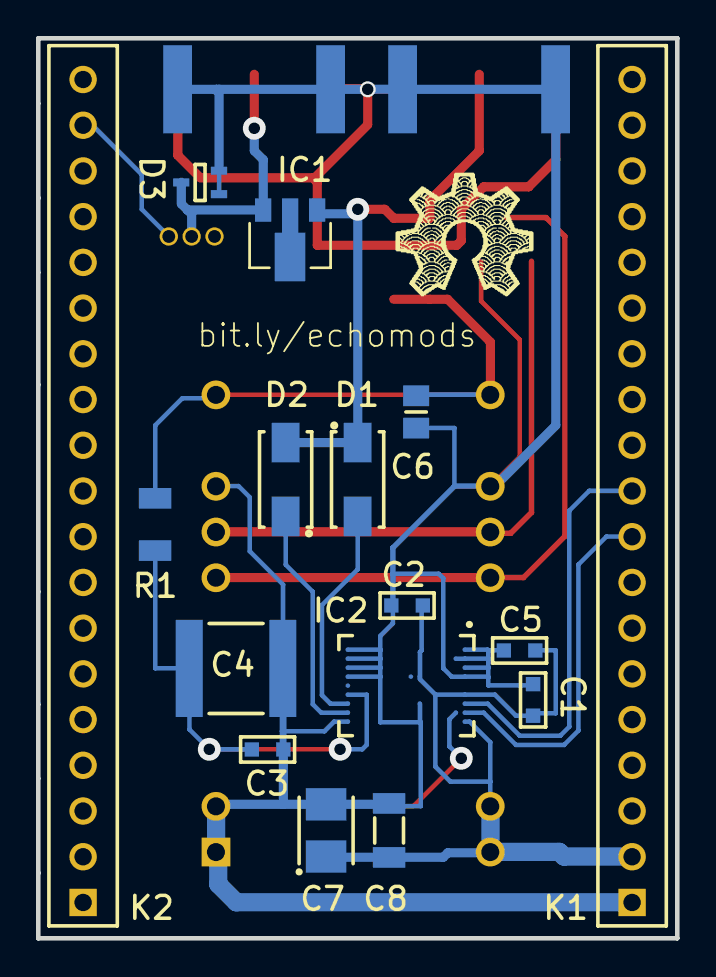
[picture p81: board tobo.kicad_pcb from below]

Board: 2 copper layers, 35.5 x 50.0 mm, 23 parts (16 on the bottom side), 13 nets.

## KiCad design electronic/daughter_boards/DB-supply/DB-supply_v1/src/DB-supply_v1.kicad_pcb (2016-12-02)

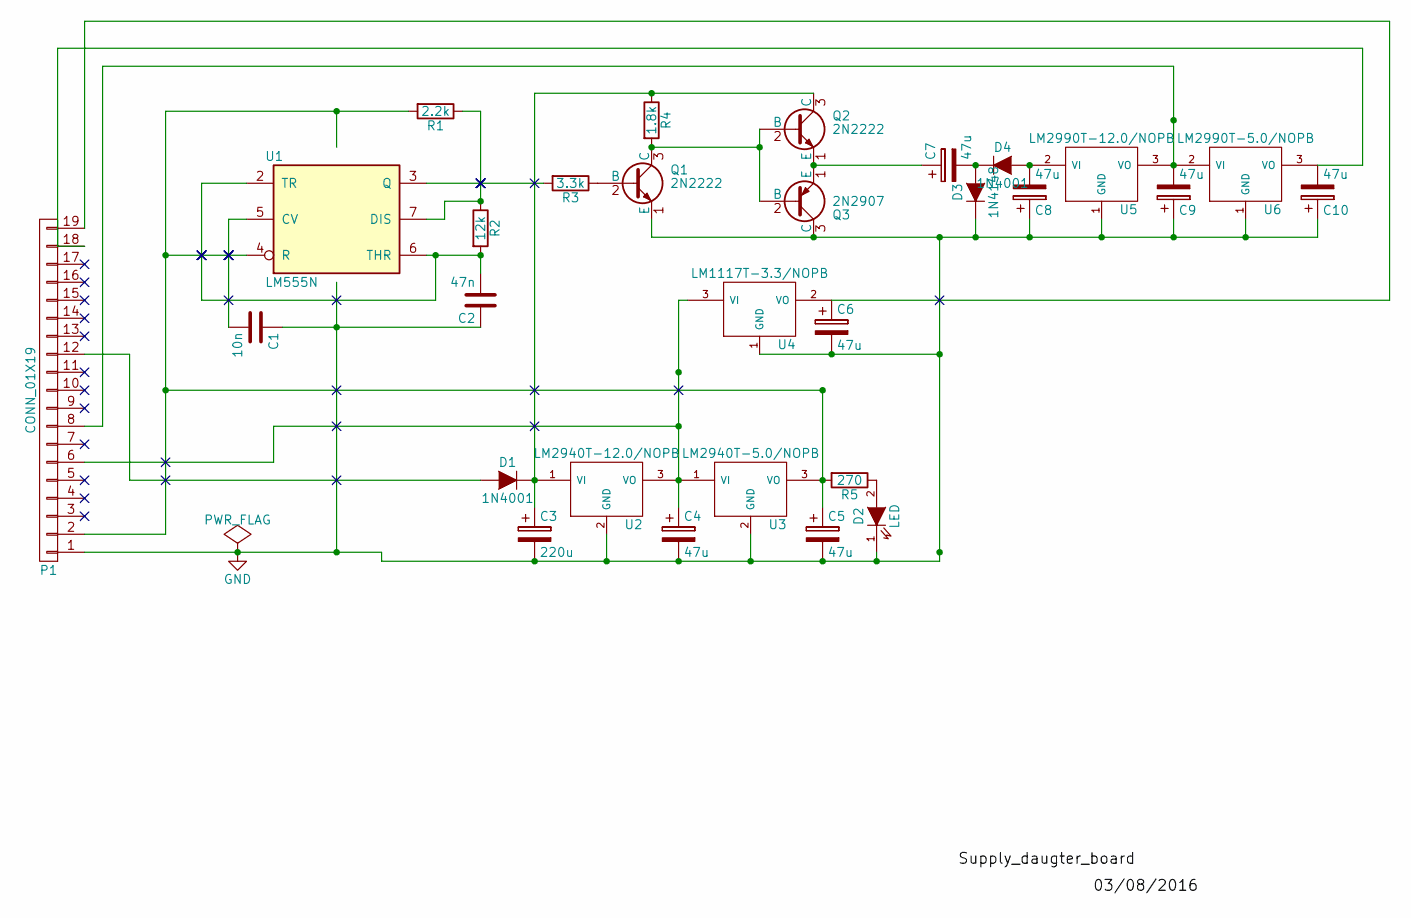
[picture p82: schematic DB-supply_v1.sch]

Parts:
C1: 10n; C_TH_common
C2: 47n; C_TH_common
C3: 220u; CP_TH_common
C4, C5, C6, C7, C8, C9, C10: 47u; CP_TH_common
D1, D4: 1N4001; D_TH_common
D2: LED; D_TH_common
D3: 1N4148; D_TH_common
P1: CONN_01X19; Header_pin_angled_1x19
Q1, Q2: 2N2222; TO-18_TH_common
Q3: 2N2907; TO-18_TH_common
R1: 2.2k; Resistor_TH_common
R2: 12k; Resistor_TH_common
R3: 3.3k; Resistor_TH_common
R4: 1.8k; Resistor_TH_common
R5: 270; Resistor_TH_common
U1: LM555N; DIP-8(LM555)
U2: LM2940T-12.0/NOPB; TO-220_TH_common
U3: LM2940T-5.0/NOPB; TO-220_TH_common
U4: LM1117T-3.3/NOPB; TO-220_TH_common
U5: LM2990T-12.0/NOPB; TO-220_TH_common
U6: LM2990T-5.0/NOPB; TO-220_TH_common

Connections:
GND: C1.1, C2.1, C3.2, C4.2, C5.2, C6.2, C8.1, C9.1, C10.1, D2.1 (K), D3.1 (K), P1.1, Q1.1 (E), Q3.3 (C), U1.1 (GND), U2.2 (GND), U3.2 (GND), U4.1 (GND), U5.1 (GND), U6.1 (GND)
unnamed: C1.2, U1.5 (CV)
unnamed: C2.2, R2.2, U1.2 (TR), U1.6 (THR)
unnamed: C3.1, D1.1 (K), Q2.3 (C), R4.1, U2.1 (VI)
unnamed: C4.1, P1.6, U2.3 (VO), U3.1 (VI), U4.3 (VI)
unnamed: C6.1, P1.19, U4.2 (VO)
unnamed: C7.1, Q2.1 (E), Q3.1 (E)
unnamed: C7.2, D3.2 (A), D4.1 (K)
unnamed: C8.2, D4.2 (A), U5.2 (VI)
unnamed: C9.2, P1.8, U5.3 (VO), U6.2 (VI)
unnamed: C10.2, P1.18, U6.3 (VO)
unnamed: D1.2 (A), P1.12
unnamed: D2.2 (A), R5.1
unnamed: Q1.2 (B), R3.1
unnamed: Q1.3 (C), Q2.2 (B), Q3.2 (B), R4.2
unnamed: R1.1, R2.1, U1.7 (DIS)
unnamed: R3.2, U1.3 (Q)
VCC: C5.1, P1.2, R1.2, R5.2, U1.4 (R), U1.8 (VCC), U3.3 (VO)


Board: 2 copper layers, 54.6 x 52.1 mm, 29 parts (0 on the bottom side), 18 nets.

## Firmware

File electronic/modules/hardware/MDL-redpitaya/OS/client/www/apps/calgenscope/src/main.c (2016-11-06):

/**
 * $Id: main.c 881 2013-12-16 05:37:34Z rp_jmenart $
 *
 * @brief Red Pitaya Oscilloscope main module.
 *
 * @Author Jure Menart <juremenart@gmail.com>
 *         
 * (c) Red Pitaya  http://www.redpitaya.com
 *
 * This part of code is written in C programming language.
 * Please visit http://en.wikipedia.org/wiki/C_(programming_language)
 * for more details on the language used herein.
 */

#include <stdio.h>
#include <unistd.h>
#include <sys/types.h>
#include <pthread.h>
#include <string.h>
#include <stdlib.h>
#include <math.h>
#include <errno.h>

#include "main.h"
#include "version.h"
#include "worker.h"
#include "fpga.h"
#include "calib.h"
#include "generate.h"

/* Describe app. parameters with some info/limitations */
pthread_mutex_t rp_main_params_mutex = PTHREAD_MUTEX_INITIALIZER;
static rp_app_params_t rp_main_params[PARAMS_NUM+1] = {
    { /* min_gui_time   */ 
        //"xmin", -1000000, 1, 0, -10000000, +10000000 },
        "xmin", 0, 1, 0, -10000000, +10000000 },
    { /* max_gui_time   */ 
        //"xmax", +1000000, 1, 0, -10000000, +10000000 },
        "xmax", 131, 1, 0, -10000000, +10000000 },
    { /* trig_mode:
       *    0 - auto
       *    1 - normal
       *    2 - single  */
        "trig_mode", 0, 1, 0,         0,         2 },
    { /* trig_source:
       *    0 - ChA
       *    1 - ChB
       *    2 - ext.    */
        "trig_source", 0, 1, 0,         0,         2 },
    { /* trig_edge:
       *    0 - rising
       *    1 - falling */
        "trig_edge", 0, 1, 0,         0,         1 },
    { /* trig_delay     */
        "trig_delay", 0, 1, 1, -10000000, +10000000 },
    { /* trig_level : Trigger level, expressed in normalized 1V  */
        "trig_level", 0, 1, 0,     -2,     +2 },
    { /* single_button:
       *    0 - ignore 
       *    1 - trigger */
        "single_btn", 0, 1, 0,         0,         1 },
    { /* time_range:
       *  decimation:
       *    0 - 1x
       *    1 - 8x
       *    2 - 64x
       *    3 - 1kx
       *    4 - 8kx
       *    5 - 65kx   */
        "time_range", 0, 1, 1,         0,         5 },
    { /* time_unit_used:
       *    0 - [us]
       *    1 - [ms]
       *    2 - [s]     */
        "time_units", 0, 0, 1,         0,         2 },
    { /* en_avg_at_dec:
           *    0 - disable
           *    1 - enable */
        "en_avg_at_dec", 0, 1, 0,      0,         1 },
    { /* auto_flag: 
       * Puts the controller to auto mode - the algorithm which detects input
       * signal and changes the parameters to most fit the input:
       *    0 - normal operation
       *    1 - auto button pressed */
        "auto_flag", 0, 1, 0, 0, 1 },
    { /* min_y, max_y - Controller defined Y range when using auto-set or after
       * gain change y range */
        "min_y", 0, 0, 0, -1000, +1000 },
    { /* min_y, max_y - Controller defined Y range when using auto-set or after
       * gain change y range */
        "max_y", 0, 0, 0, -1000, +1000 },
    { /* forcex_flag: 
       * Server sets this flag when X axis time units change
       * Client checks this flag, when set the server's xmin:xmax define the visualization range 
       *    0 - normal operation
       *    1 - Server forces xmin, xmax  */
        "forcex_flag", 0, 0, 0, 0, 1 },	
      /* Measurement parameters for both channels. All are read-only and they
       * are calculated on FPGA buffer (non decimated in SW):
       * min, max [V] - minimum and maximum value in the buffer (non-decimated)
       * amp [Vpp] - amplitude = maximum - minum
       * avg [V] - average value
       * freq [MHz] - frequency of the signal (if any, otherwise NaN)
       * period [s] - period of the signal (if any, otherwise NaN)
       **/
    {  "meas_min_ch1", 0, 0, 1, -1000, +1000 },
    {  "meas_max_ch1", 0, 0, 1, +1000, -1000 },
    {  "meas_amp_ch1", 0, 0, 1, +1000, -1000 },
    {  "meas_avg_ch1", 0, 0, 1, +1000, -1000 },
    {  "meas_freq_ch1", 0, 0, 1, 0, 1e9 },
    {  "meas_per_ch1", 0, 0, 1, 0, 1e9 },
    {  "meas_min_ch2", 0, 0, 1, -1000, +1000 },
    {  "meas_max_ch2", 0, 0, 1, +1000, -1000 },
    {  "meas_amp_ch2", 0, 0, 1, +1000, -1000 },
    {  "meas_avg_ch2", 0, 0, 1, +1000, -1000 },
    {  "meas_freq_ch2", 0, 0, 1, 0, 1e9 },
    {  "meas_per_ch2", 0, 0, 1, 0, 1e9 },
    { /* prb_att_ch1 - User probe attenuation setting for channel 1:
       *    0 - 1x
       *    1 - 10x */
        "prb_att_ch1", 0, 1, 0, 0, 1 },
    { /* gain_ch1 - User jumper gain setting for channel 1:
       *    0 - high gain (0.6 [V] Full-scale)
       *    1 - low gain (15 [V] Full-scale) */
        "gain_ch1", 0, 1, 0, 0, 1 },
    { /* prb_att_ch2 - User probe attenuation setting for channel 2:
       *    0 - 1x
       *    1 - 10x */
        "prb_att_ch2", 0, 1, 0, 0, 1 },
    { /* gain_ch2 - User jumper gain setting for channel 2:
       *    0 - high gain (0.6 [V] Full-scale)
       *    1 - low gain (15 [V] Full-scale) */
        "gain_ch2", 0, 1, 0, 0, 1 },
    { /* gui_reset_y_range - Maximum voltage range [Vpp] with current settings
       * This parameter is calculated by application and is read-only for
       * client.
       */
        "gui_reset_y_range", 28, 0, 1, 0, 2000 },
    { /* gen_DC_offs_1 - DC offset for channel 1 expressed in [V] requested by 
       * GUI */
        "gen_DC_offs_1", 0, 1, 0, -100, 100 },
    { /* gen_DC_offs_2 - DC offset for channel 2 expressed in [V] requested by 
       * GUI */
        "gen_DC_offs_2", 0, 1, 0, -100, 100 },
    { /* gui_xmin - Xmin as specified by GUI - not rounded to sampling engine quanta. */
        "gui_xmin",      0, 0, 1, -10000000, +10000000 },
    { /* gui_xmax - Xmax as specified by GUI - not rounded to sampling engine quanta. */
        "gui_xmax",    131, 0, 1, -10000000, +10000000 },
    { /* min_y_norm, max_y_norm - Normalized controller defined Y range when using auto-set */
        "min_y_norm", 0, 0, 0, -1000, +1000 },
    { /* min_y_norm, max_y_norm - Normalized controller defined Y range when using auto-set */
        "max_y_norm", 0, 0, 0, -1000, +1000 },
    { /* gen_DC_norm_1 - DC offset for channel 1 expressed in normalized 1V */
        "gen_DC_norm_1", 0, 1, 0, -100, 100 },
    { /* gen_DC_norm_2 - DC offset for channel 2 expressed in normalized 1V */
        "gen_DC_norm_2", 0, 1, 0, -100, 100 },
    { /* scale_ch1 - Jumper & probe attenuation dependent Y scaling factor for Channel 1 */
        "scale_ch1", 0, 0, 1, -1000, 1000 },
    { /* scale_ch2 - Jumper & probe attenuation dependent Y scaling factor for Channel 2 */
        "scale_ch2", 0, 0, 1, -1000, 1000 },
    { /* dc_cal - DC offset calibration button (toggled) */
        "dc_cal", 0, 1, 0, 0, 1 },	
    { /* req_trc - Data trace download button (toggled) */
        "req_trc", 0, 1, 0, 0, 1 }, 
    { /* dc_calout1 - DC offset calibration button for out 1 (toggled) */
        "dc_calout1", 0, 1, 0, 0, 1 },		
    { /* dc_calout2 - DC offset calibration button for out 2 (toggled) */
        "dc_calout2", 0, 1, 0, 0, 1 },			
    /* Arbitrary Waveform Generator parameters from here on */

    { /* gen_trig_mod_ch1 - Selects the trigger mode for channel 1:
       *    0 - continuous
       *    1 - single 
       *    2 - external */
        "gen_trig_mod_ch1", 0, 1, 0, 0, 2 },
    { /* gen_sig_type_ch1 - Selects the type of signal for channel 1:
       *    0 - sine
       *    1 - square
       *    2 - triangle
       *    3 - from file */
        "gen_sig_type_ch1", 0, 1, 0, 0, 3 },
    { /* gen_enable_ch1 - Enables/disable signal generation on channel 1:
       *    0 - Channel 1 disabled
       *    1 - Channel 1 enabled */
        "gen_enable_ch1", 0, 1, 0, 0, 1 },
    { /* gen_single_ch1 - Fire single trigger on generator channel 1:
       *    0 - Do not fire single trigger
       *    1 - Fire single trigger */
        "gen_single_ch1", 0, 1, 0, 0, 1 },
    { /* gen_sig_amp_ch1 - Amplitude for Channel 1 in [Vpp] */
        "gen_sig_amp_ch1", 0, 1, 0, 0, 2.0 },
    { /* gen_sig_freq_ch1 - Frequency for Channel 1 in [Hz] */
        "gen_sig_freq_ch1", 1000, 1, 0, 0, 50e6 },
    { /* gen_sig_dcoff_ch1 - DC offset applied to the signal in [V] */
        "gen_sig_dcoff_ch1", 0, 1, 0, -1, 1 },
    { /* gen_trig_mod_ch2 - Selects the trigger mode for channel 2:
       *    0 - continuous
       *    1 - single 
       *    2 - external */
        "gen_trig_mod_ch2", 0, 1, 0, 0, 2 },
    { /* gen_sig_type_ch2 - Selects the type of signal for channel 2:
       *    0 - sine
       *    1 - square
       *    2 - triangle
       *    3 - from file */
        "gen_sig_type_ch2", 0, 1, 0, 0, 3 },
    { /* gen_enable_ch2 - Enables/disable signal generation on channel 2:
       *    0 - channel 2 disabled
       *    1 - channel 2 enabled */
        "gen_enable_ch2", 0, 1, 0, 0, 1 },
    { /* gen_single_ch2 - Fire single trigger on generator channel 2:
       *    0 - Do not fire single trigger
       *    1 - Fire single trigger */
        "gen_single_ch2", 0, 1, 0, 0, 1 },
    { /* gen_sig_amp_ch2 - Amplitude for channel 2 in [Vpp] */
        "gen_sig_amp_ch2", 0, 1, 0, 0, 2.0 },
    { /* gen_sig_freq_ch2 - Frequency for channel 2 in [Hz] */
        "gen_sig_freq_ch2", 1000, 1, 0, 0.2, 50e6 },
    { /* gen_sig_dcoff_ch2 - DC offset applied to the signal in [V] */
        "gen_sig_dcoff_ch2", 0, 1, 0, -1, 1 },
    { /* gen_awg_refresh - Refresh AWG data from (uploaded) file.
       *     0 - Do not refresh
       *     1 - Refresh Channel 1
       *     2 - Refresh Channel 2
       */
        "gen_awg_refresh",   0, 0, 0, 0, 2 },
    { /* Must be last! */
        NULL, 0.0, -1, -1, 0.0, 0.0 }     
};
/* params initialized */
static int params_init = 0;

/* AUTO set algorithm in progress flag */
int auto_in_progress = 0;

rp_calib_params_t rp_main_calib_params;

int forcex_state = 0;
float forced_xmin = 0;
float forced_xmax = 0;
float forced_units = 0;
float forced_delay = 0;


const char *rp_app_desc(void)
{
    return (const char *)"Red Pitaya osciloscope application.\n";
}

int rp_app_init(void)
{
    fprintf(stderr, "Loading scope (with gen+pid extensions) version %s-%s.\n", VERSION_STR, REVISION_STR);

    rp_default_calib_params(&rp_main_calib_params);
    if(rp_read_calib_params(&rp_main_calib_params) < 0) {
        fprintf(stderr, "rp_read_calib_params() failed, using default"
                " parameters\n");
    }
    if(rp_osc_worker_init(&rp_main_params[0], PARAMS_NUM, 
                          &rp_main_calib_params) < 0) {
        return -1;
    }
    if(generate_init(&rp_main_calib_params) < 0) {
        return -1;
    }

    rp_set_params(&rp_main_params[0], PARAMS_NUM ,0);


    return 0;
}

int rp_app_exit(void)
{
    fprintf(stderr, "Unloading scope (with gen+pid extensions) version %s-%s.\n", VERSION_STR, REVISION_STR);

    rp_osc_worker_exit();
    generate_exit();

    return 0;
}

int time_range_to_time_unit(int range)
{
    int unit = 2;
    
    switch (range) {
    case 0:
    case 1:
        unit = 0;
        break;
    case 2:
    case 3:
        unit = 1;
        break;
    default:
        unit = 2;
    }

    return unit;
}
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

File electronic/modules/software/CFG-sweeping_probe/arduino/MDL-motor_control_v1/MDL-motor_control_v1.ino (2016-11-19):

#define NOP __asm__ __volatile__ ("nop\n\t")

//volatile for interrupt
volatile float MotorVelocity=3.0;
volatile unsigned long t10=0, t11=0;
volatile double Deltat;
volatile int PinDecodeur=2; //conteur pour se caler sur le même capteur
double Cv=0.052*6.283185307;

int pwm=200;  //motor pwm
int stateold=LOW, statenew=LOW; //state of motor encoder
int tourold=LOW, tournew=LOW; //state of mecaniq encoder
int pinpwm=5; //Pin for motor pwm
int pinA=2; //Pin for moteur encoder
int PinTour=7; //Pin for half tour encoder
int PinLED=9; //Pin for pulse
double Vlim=2.0/1000000.0*6.283185307;//2.8

// position variables
const int N=64; //number of line
volatile double phi[N-1]; //angle of the motor
volatile double dphi[N];  //delta phi between lines
int pos=0;  //number of the line
unsigned int dt; //delta t between lines

void Pulse(){
  PORTB = B00010010;
  NOP;
  PORTB = B00000000;//pulse 125 ns long
}

void Velocity(){
  PinDecodeur++;
  if (PinDecodeur==1){
    /* there is 3 detector per tour in the encoder not equaly space
     * so we take only one to be sure un tour is done
     */
    t11=micros();
    Deltat=(double)(t11-t10);
    MotorVelocity=Cv/Deltat; //velocity in radian per us
    t10=t11;
    if(MotorVelocity>Vlim) {
      pwm--;
      MotorVelocity=Vlim;
      }
    else{pwm++;}
    analogWrite(pinpwm,pwm);
  }
  if (PinDecodeur==3){PinDecodeur=0;}
}

void Interpolation(){
  for (int i=0 ; i<N ;i++){
    phi[i]=asin(2.0*i/(N-1.0)-1.0);
  }
  dphi[0]=phi[N/2];
  for (int i=1 ; i<N/2 ; i++){dphi[i]=phi[N/2+i]-phi[N/2+i-1];}
  for (int i=N/2 ; i<N-1 ; i++){dphi[i]=dphi[N-1-i];}
  for (int i=0 ; i<N-1 ; i++){
  }
  /*for (int i=0 ; i<N-1 ; i++){
    Serial.print(dphi[i]);
    Serial.print("\n");
  }*/
}

void setup() {
  // put your setup code here, to run once:
  pinMode(pinpwm,OUTPUT);
  DDRB = B00010010;//pinMode(PinLED,OUTPUT);
  pinMode(PinTour,INPUT);
  pinMode(pinA,INPUT);
  Serial.begin(115200);
  analogWrite(pinpwm,pwm);
  Interpolation();
  attachInterrupt(digitalPinToInterrupt(2), Velocity, RISING);
}

void loop() {
  // put your main code here, to run repeatedly:
  pos=0;

  tournew=digitalRead(PinTour);
  if(tournew==HIGH && tourold==LOW){
        while (pos<N/2){
      dt=(unsigned int)(dphi[pos]/MotorVelocity);
      if (dt>20000){
        // empiricaly it is more precise to do like that...
        delayMicroseconds(10000);
        delayMicroseconds(10000);
        delayMicroseconds(dt-20001);
      }
      else if(dt>10000){
        delayMicroseconds(10000);
        delayMicroseconds(dt-10001);
      }
      else{delayMicroseconds(dt-1);}
      Pulse();
      pos++;
    }
}
  if(tournew==LOW && tourold==HIGH){
        while (pos<N/2){
      dt=(unsigned int)(dphi[pos]/MotorVelocity);
      if (dt>20000){
        delayMicroseconds(10000);
        delayMicroseconds(10000);
        delayMicroseconds(dt-20001);
      }
      else if(dt>10000){
        delayMicroseconds(10000);
        delayMicroseconds(dt-10001);
      }
      else{delayMicroseconds(dt-1);}
      Pulse();
      pos++;
    }
  }
  tourold=tournew;
}

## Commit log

2016-10-06 Update file structure
    [2015-11-29 sonde_complete_v1.FCStd, 2015-11-29 sonde_complete_v2.FCStd, 2015-11-29 sonde_complete_v3.0.FCStd, 2015-11-29 sonde_complete_v3.1.FCStd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]
2016-10-07 testing module documentation
    [2015-11-29 sonde_complete_v1.FCStd, 2015-11-29 sonde_complete_v2.FCStd, 2015-11-29 sonde_complete_v3.0.FCStd, 2015-11-29 sonde_complete_v3.1.FCStd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]
2016-10-14 Update file structure, work in progress !
    [MDL-filter_v1.csv, MDL-filter_v1.kicad_pcb, MDL-filter_v1.sch, MDL-filter_v2.csv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]
2016-10-27 update modules repo
    [MDL-envelope_detector_v1.csv, MDL-envelope_detector_v1.kicad_pcb, MDL-envelope_detector_v1.sch, MDL-filter_v1.csv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]
2016-11-01 update modules
    [MDL-envelope_detector_v1.sch, MDL-filter_v1.sch, MDL-filter_v2.sch, MDL-hvc_v1.sch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]
2016-11-03 update modules and daughter boards
    [DB_Envelope_detector_V1-B.Cu.gbr, DB_Envelope_detector_V1-B.Mask.gbr, DB_Envelope_detector_V1-B.SilkS.gbr, DB_Envelope_detector_V1-F.Cu.gbr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]
2016-11-04 update documentation
    [DB-envelope_detector_v1-B.Cu.gbl, DB-envelope_detector_v1-B.Mask.gbs, DB-envelope_detector_v1-B.SilkS.gbo, DB-envelope_detector_v1-Edge.Cuts.gm1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]
2016-11-05 update daughter boards documentation
    [DB-motor_control_v1.csv, DB-motor_control_v1.sch, DB-motor_control_v2.csv, DB-pulser_v2.csv]
2016-11-09 reworking repos
    [2015-11-29 sonde_complete_v1.FCStd, 2015-11-29 sonde_complete_v2.FCStd, 2015-11-29 sonde_complete_v3.0.FCStd, 2015-11-29 sonde_complete_v3.1.FCStd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]
2016-11-10 deleting double files
    [2015-11-29 sonde_complete_v1.FCStd, 2015-11-29 sonde_complete_v2.FCStd, 2015-11-29 sonde_complete_v3.0.FCStd, 2015-11-29 sonde_complete_v3.1.FCStd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]
2016-12-02 update src of DBs
    [BOM.csv, DB-envelope_detector_v1-B.Cu.gbl, DB-envelope_detector_v1-B.Mask.gbs, DB-envelope_detector_v1-B.Paste.gbp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]
2016-12-19 Adding some ICs modules
    [20160928-151602-0.csv, 20160928-151602-1.csv, 20160928-152035-0.csv, 20160928-152035-1.csv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]
2016-12-19 Adding the CFG-arduino_servo
2016-12-21 adding motor_control_v3
    [DB-motor_control_v2-B.Cu.gbl, DB-motor_control_v2-B.Mask.gbs, DB-motor_control_v2-B.SilkS.gbo, DB-motor_control_v2-Edge.Cuts.gm1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]
2017-01-24 adding motor_control_v3 and trs_tgc_v2
    [DB-motor_control_v3-drl_map.gbr, DB-motor_control_v3.csv, DB-motor_control_v3.drl, DB-motor_control_v3.kicad_pcb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]
2017-02-21 adding new pulser board
    [BOM.csv, DB-pulser_v1-B.Cu.gbl, DB-pulser_v1-B.Mask.gbs, DB-pulser_v1-B.Paste.gbp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]
2017-03-07 update pulser ref
    [DB-pulser_v3.sch]
2017-04-07 sorting codes
    [DB-motor_control_v3.sch, MDL-pulser_v2.sch, RS_BOM.csv]
2017-04-07 correct MDL pulser and update DB motor control
    [DB-motor_control_v3-B.Cu.gbr, DB-motor_control_v3-B.SilkS.gbr, DB-motor_control_v3-Edge.Cuts.gbr, DB-motor_control_v3-F.Cu.gbr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]
2017-04-10 cleaning repos
    [20160928-151602-0.csv, 20160928-151602-1.csv, 20160928-152035-0.csv, 20160928-152035-1.csv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]
2017-04-12 adding motor_control_v3 documentation
    [DB-motor_control_v3.kicad_pcb, DB-motor_control_v3.sch, MDL-motor_support.stl, MDL-phantom_support_1.stl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]
2017-05-19 adding MDL uc_v3
    [MDL-ucontroler_v1.kicad_pcb, MDL-ucontroler_v1.sch]
2017-05-19 update config
    [MDL-high_voltage_v1.csv, MDL-high_voltage_v1.kicad_pcb, MDL-high_voltage_v1.sch, MDL-high_voltage_v2.csv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]
2017-05-24 Documentation static web site regenerated.
    [20161217-222737-0.csv, 20161217-222737-1.csv, 20161217-222737-2.csv, 20161217-222737-3.csv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]
2017-07-12 update DB-motor_control_v3
    [DB-motor_control_v3.csv, DB-pulser_v3.csv]
2017-07-12 update DB-motor_control_v3 2
2017-12-18 update instalation doc
    [DB-pulser_v3-B.Cu.gbr, DB-pulser_v3-B.Mask.gbr, DB-pulser_v3-B.SilkS.gbr, DB-pulser_v3-Edge.Cuts.gbr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]
